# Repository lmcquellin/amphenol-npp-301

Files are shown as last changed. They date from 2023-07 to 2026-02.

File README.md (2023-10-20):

# Use of Amphenol NPP-301 Series Pressure Transducers for Pressure Measurements

## 1. Overview
The NPP-301 series of pressure sensors manufactured by Amphenol Advanced Sensors have demonstrated to be a low cost means of collecting discrete pressure measurements in space constrained locations on wind tunnel models. The transducer is offered in three pressure ranges, 0 – 100 kPa, 0 - 200 kPa, and 0 – 700 kPa.

## 2. Electrical Characteristics

Figure 1 presents the electrical schematic of the NPP-301 as supplied by Amphenol. The large variation in transducer input and output impedance (20% [1]) results in a large amount of transducer-to-transducer variation. Additionally, because the operating pressure can be an order of magnitude lower than the rated pressure, the transducer is having to operate at the extremity of its operating range. The split negative input pins (Pins 4 & 5) allow for the bridge to be compensated through the use of an additional resistor. This compensation allows for the bridge to be balanced at a desired pressure. This has two effects. First, the balanced bridge means that the bridge output voltage is minimised, allowing for greater amplifier dynamic range. Secondly, the bridge compensation process reduces the large variation in transducer output performance between sensors, allowing for simpler amplifiers to be used.

## 3. Frequency Response

Frequency response has not been characterised, but is estimated to be on the order of several kilohertz.

## 4. Bridge Compensation

Bridge compensation is performed using a vacuum cell with a 5 wire feed-through, a mounting PCB or carrier board for connecting to the sensor and a digital multimeter. Details of calibration carrier boards are provided in appendix A.

Bridge compensation is performed as follows:
* If not mounted to a PCB, transducer body is marked for identification. If mounted to a PCB, PCB is typically marked. Transducer is then placed in the integrated circuit socket.
* Mounting PCB or test socket is interconnected through the vacuum cell feed-through, with 5 flying-lead wires available externally for measurement connections.
* Vacuum cell is evacuated to the desired compensation pressure. This is typically $\<$ 100 Pa for wind tunnel testing with evacuated test sectionbs. Ambient temperature during the calibration should also be recorded.
* The following resistances are then measured between pin pairs on the transducer body, using externally available wires. Pin 8 & 2, Pin 8 & 6, Pin 2 & 4, and Pin 6 & 5. Resistance values will typically be in the 4500 - 4900 Ω range and should be recorded to the nearest ohm.

This procedure is repeated for each transducer with the results being populated in a text file called 'resistor_data.txt'. File should be TAB delimited. The resistor_data text file takes the following format:
'''
PIN 8/2  PIN 8/6	PIN 2/4	PIN 6/5
'''

Again, resistance of each measurement element should be recorded in ohms to the nearest ohm. An example have been provided in 'resistor_data.txt'. Once complete, the compensation values for each individual transducer can be determined. To do this, the MATLAB script 'npp_comp.m' is used. Note: 'npp_comp.m' requires 'resval.mat' in order to run successfully. 'resval.mat' is also provided as a comma-separated values file. The script, when run, will evaluate all resistance values present in the 'resistor_data.txt' data file. For each transducer, a suggested compensation resistor value will be provided based on commercially available resistance values (contained in 'resval.mat'), and the branch of the wheatstone bridge this resistance should be provided. The script will also provide a bridge output voltage (Vb) for a given bridge input voltage at the compensated pressure. It is advised that the reported resistance is then recorded in a transducer calibration register (see 'npp_calibration_register_blank.ods') as this will be cleared from the screen when the script is run again. The following provides an example of the script output for a transducer with the values PIN 8/2 = 4726, PIN 8/6 = 4752 PIN 2/4 = 4769 PIN 6/5 = 4742.

```
------
OUTPUT
------
Input Voltage: 5V
Suggested Compensation Resistance: 51 Ohms
Compensation on Leg: 865
Vb: 0.58314 mV
```
Figure 3 presents a revised schematic that includes the compensation resistor and its position within the circuit. It can be seen that the compensation resistor is connected between pins 4 & 5, with the IN- connection point becoming pin 4. Depending on the mounting configuration, the means in which this resistor can be included into the pressure transducer can vary. Two methods are presented here, PCB mounting (subsection 5.1) and ’deadbug’ mounting (subsection 5.2).

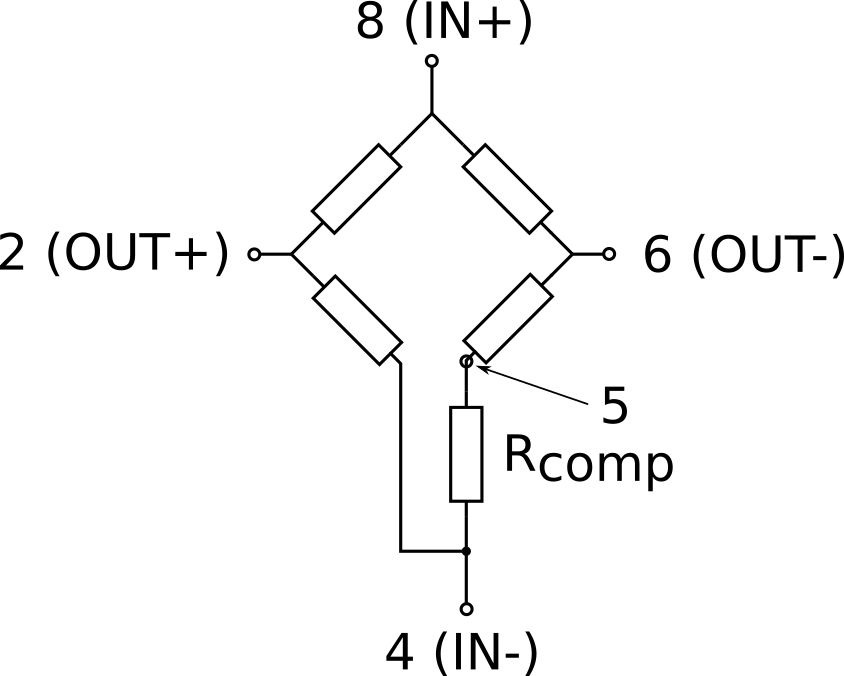
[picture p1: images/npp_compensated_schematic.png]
NPP_Compensated_Schematic


## 5. Packaging and Mounting

The NPP-301 is available in a small-outline 8 (SO8) surface mount package with either a barbless (NPP-301A) or barbed (NPP-301B) pressure port [1]. Dimensions of the barbed and barbless packaging are
available in appendix A. Two mounting options have been explored thus far. Printed circuit board (PCB) mounting and ‘deadbug’ mounting.

### 5.1 PCB Mounting

PCB mounting allows for a transducer to be rigidly mounted to a structure with fasteners. Multiple transducers can also be mounted to a single PCB to simplify interconnectivity and maximise measurement density. The SO8 package size and placement of the barb limits the pitch of an array of transducers to 8 mm. An example of a transducer mounted to a single PCB is provided in Fig. 4. This arrangement where the transducer body is offset from the horizontal centreline of the PCB is done so to place the barb in the horizontal and vertical centre of the board. Four mounting holes suitable for M1.6 fasteners are used in each corner. On the reverse side of the PCB; pads for soldered wire connections are provided, along with pads for surface mount 0402 size compensation resistors. To ensure a adequate pressure connection between the pressure port of the sensor and the pressure tap on the surface of the model, a BS003 o-ring is used to provide a seal. Geometry for the o-ring groove is provided in appendix B. Typical dimensions of a single transducer mounting PCB is also provided in appendix B.

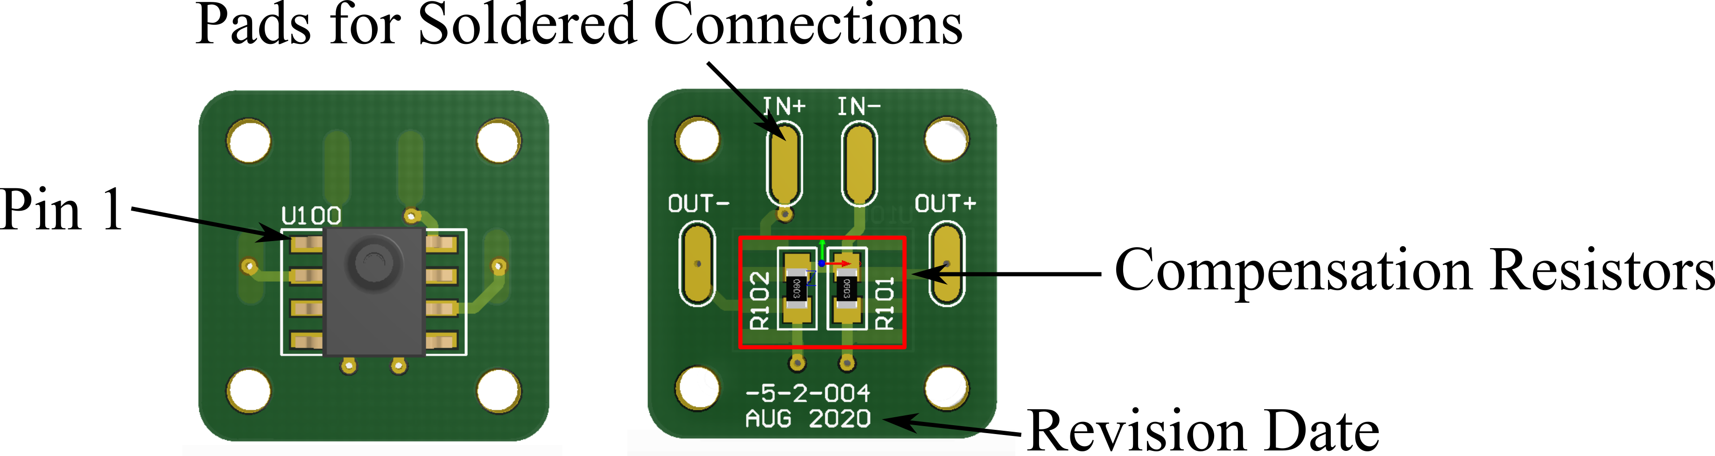
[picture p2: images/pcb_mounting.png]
NPP_PCB_Mounting


### 5.2 Deadbug Mounting

Deadbug mounting, named due to the appearance of an integrated circuit package body upside down, is the other proposed method for interconnecting and mounting the transducer. This mounting type is the most volumetrically efficient, but is more time consuming the manufacture and mounting into a model is permanent. Instructions to assembly a transducer body with wire is provided in appendix C. Transducer bodies are typically bonded into cavities or against panels using epoxy (or other suitable) adhesive. This is depicted in Fig. 5. When using the barbless ‘A’ package, ensuring concentricity between the pressure tap in the panel and port in the transducer can be achieved by using a machined locating pin to locate the transducer during assembly. When using the barbed ‘B’ package, a countersink in the surface is required to accommodate the barb. This countersink ensures port concentricity during mating.

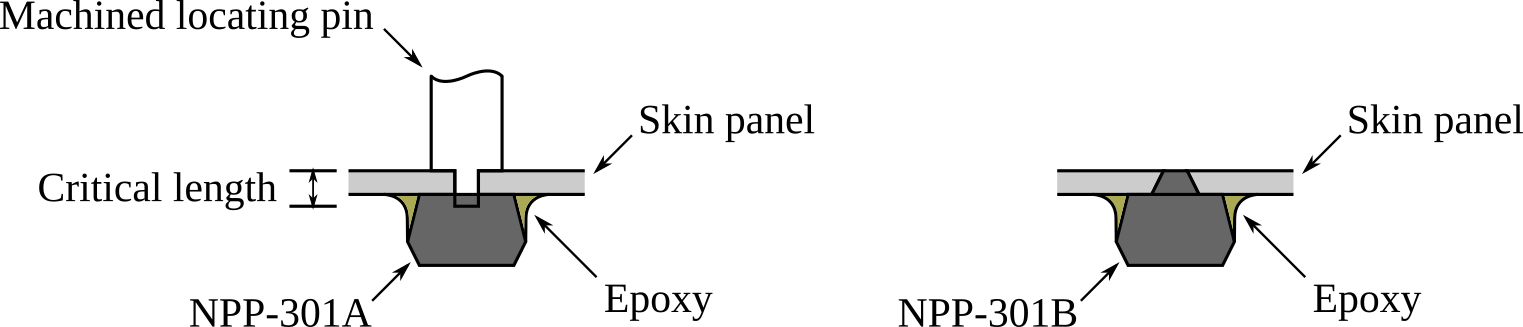
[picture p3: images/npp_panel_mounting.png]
NPP_Panel_Mounting


## References

[1] Amphenol Advanced Sensors. NPP-301 Series Surface Mount Pressure Sensor, 3 2019. web: https://www.amphenol-sensors.com/hubfs/Documents/AAS-920-297B-NovaSensor-NPP-301-031414-web.pdf

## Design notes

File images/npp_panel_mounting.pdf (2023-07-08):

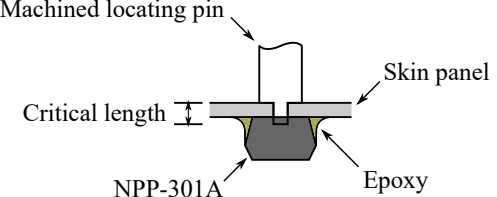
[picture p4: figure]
NPP-301A; Machined locating pin; Skin panel; Epoxy; Critical length
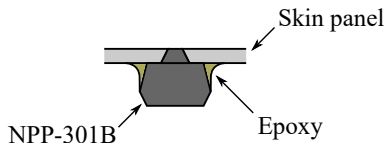
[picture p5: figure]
Skin panel; NPP-301B; Epoxy

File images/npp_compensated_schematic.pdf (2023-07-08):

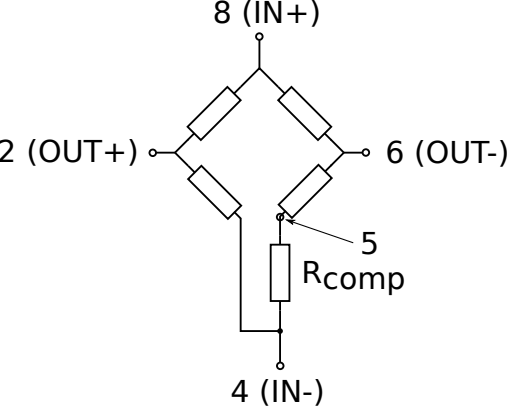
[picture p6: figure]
Rcomp; 2 (OUT+); 6 (OUT-)

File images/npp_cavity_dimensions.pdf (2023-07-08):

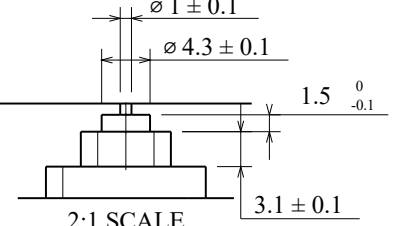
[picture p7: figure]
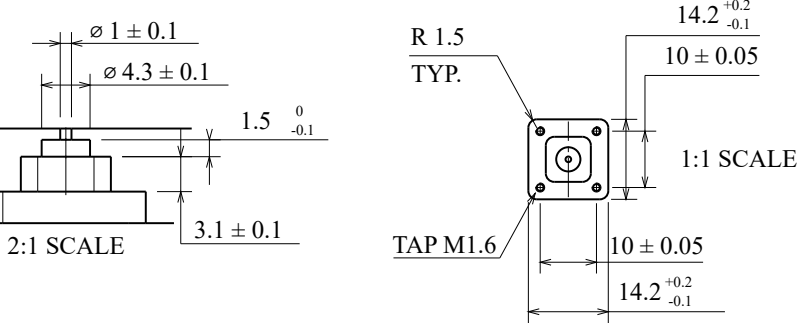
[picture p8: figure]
R 1.5 TYP.; 2:1 SCALE; TAP M1.6; 1:1 SCALE

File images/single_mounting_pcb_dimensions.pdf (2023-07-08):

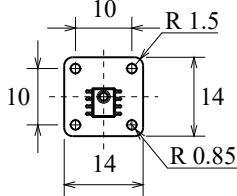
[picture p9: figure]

4.5

1.2

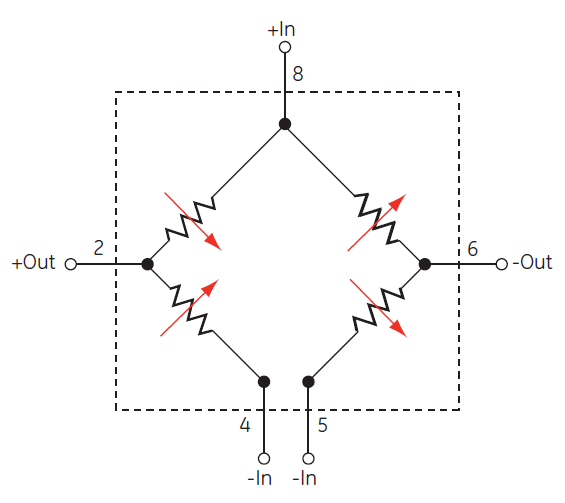
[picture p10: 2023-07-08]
images/npp301_schematic.png

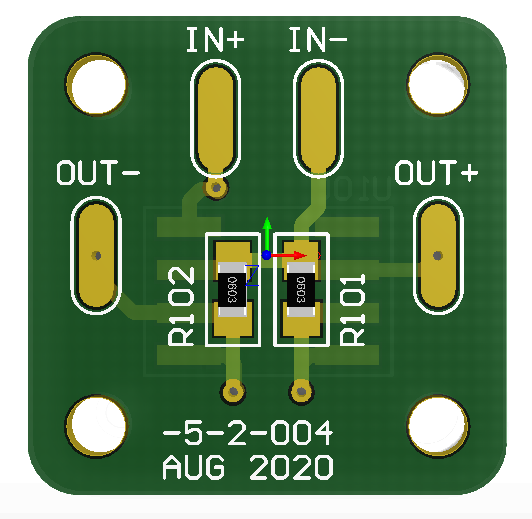
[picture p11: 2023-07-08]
images/npp301b_render_b.png

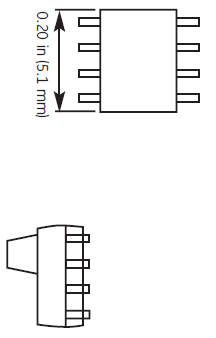
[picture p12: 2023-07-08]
images/301a.png

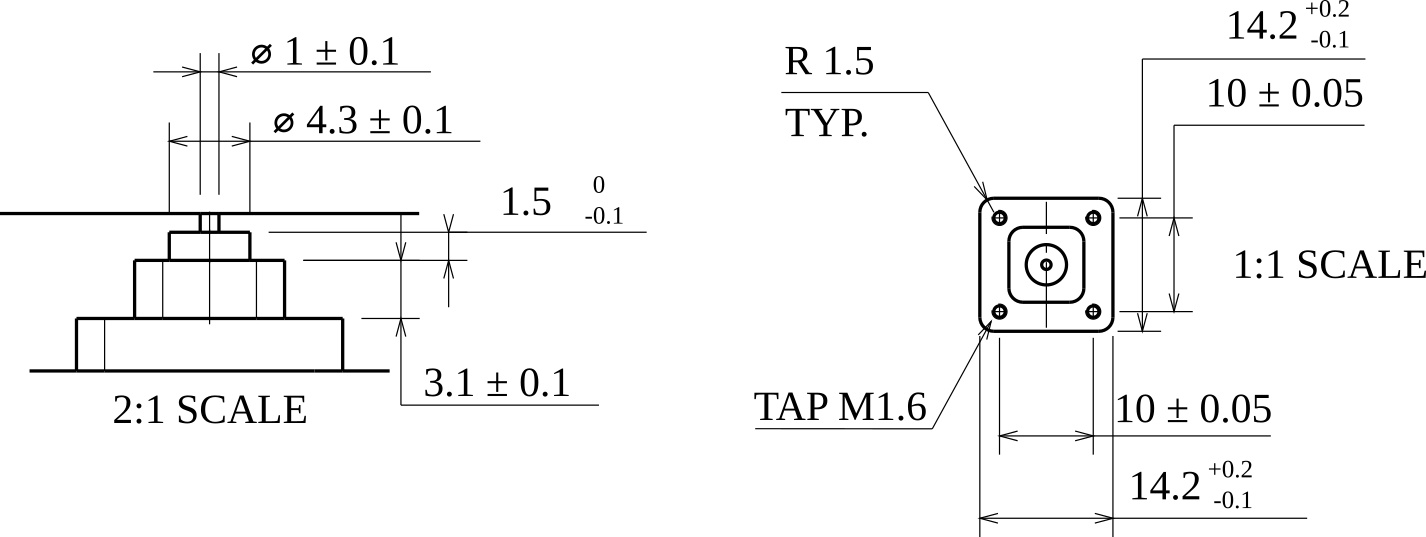
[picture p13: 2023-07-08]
images/npp_cavity_dimensions.png

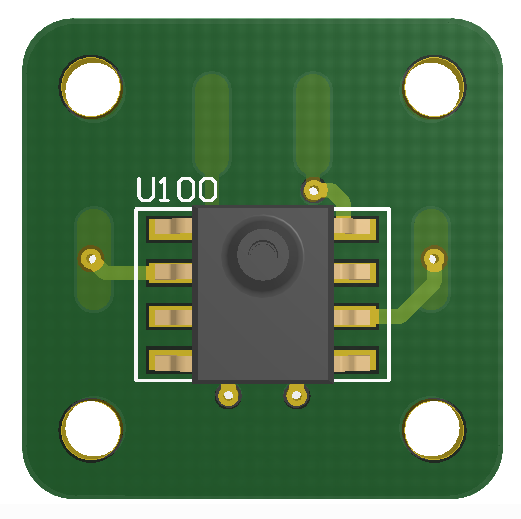
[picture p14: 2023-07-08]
images/npp301b_render_a.png

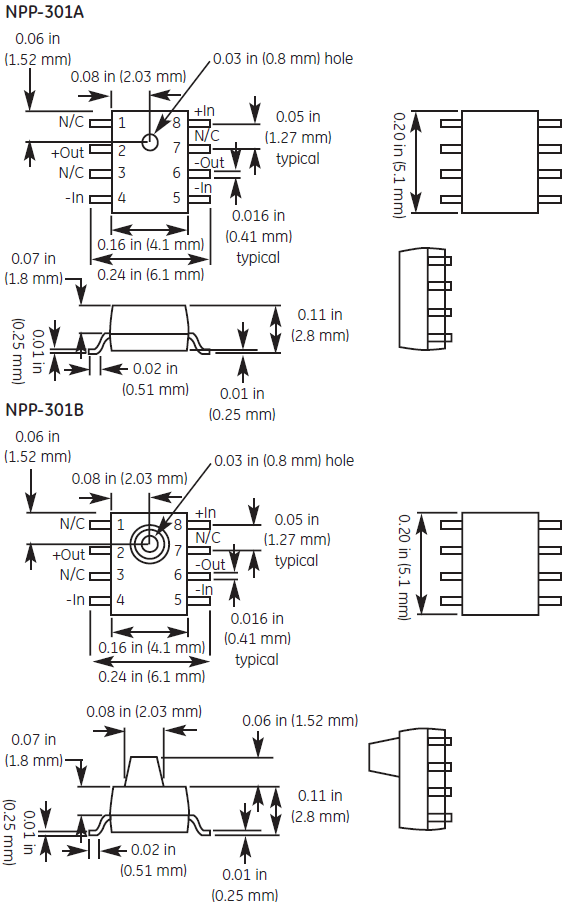
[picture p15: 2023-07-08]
images/npp301_packaging.png

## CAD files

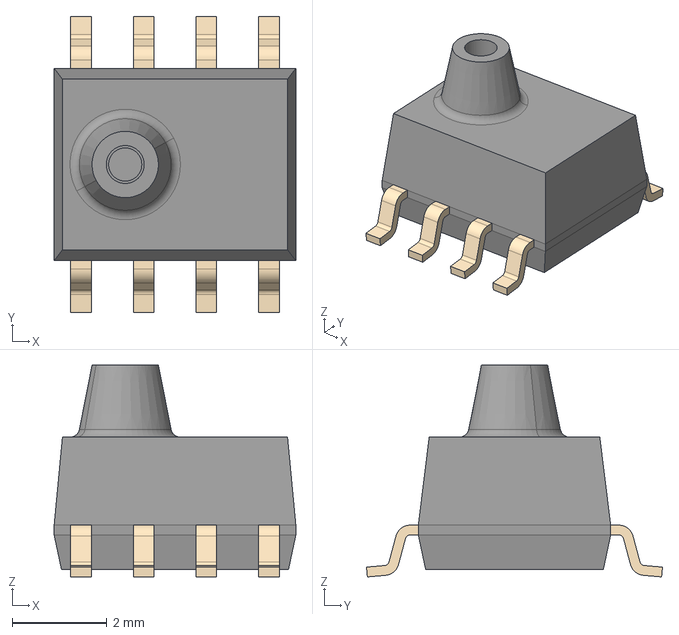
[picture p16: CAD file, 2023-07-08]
3dmodels/npp_301b.stp
5.10 x 6.24 x 4.47 mm

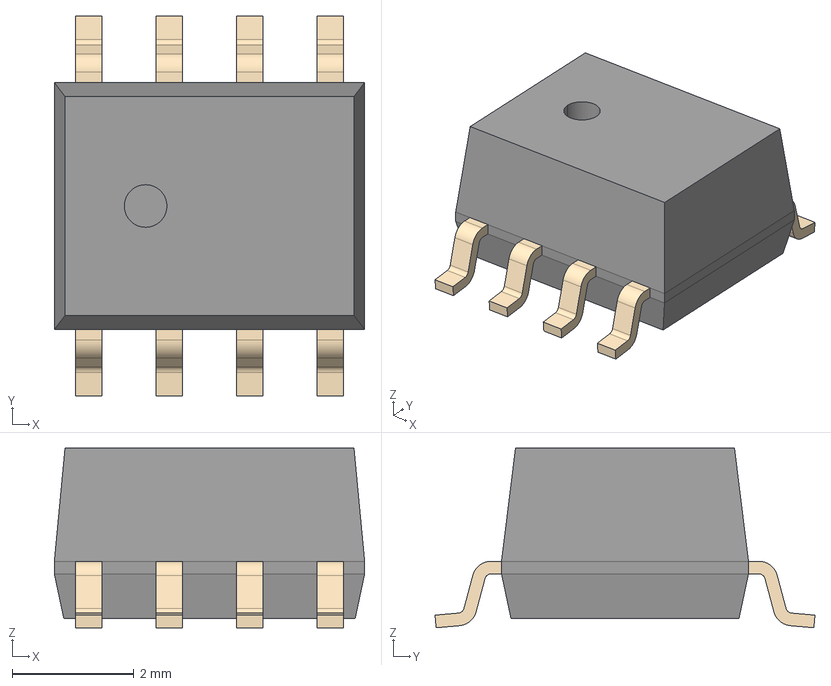
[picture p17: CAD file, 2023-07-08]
3dmodels/npp_301a.stp
5.10 x 6.24 x 2.95 mm

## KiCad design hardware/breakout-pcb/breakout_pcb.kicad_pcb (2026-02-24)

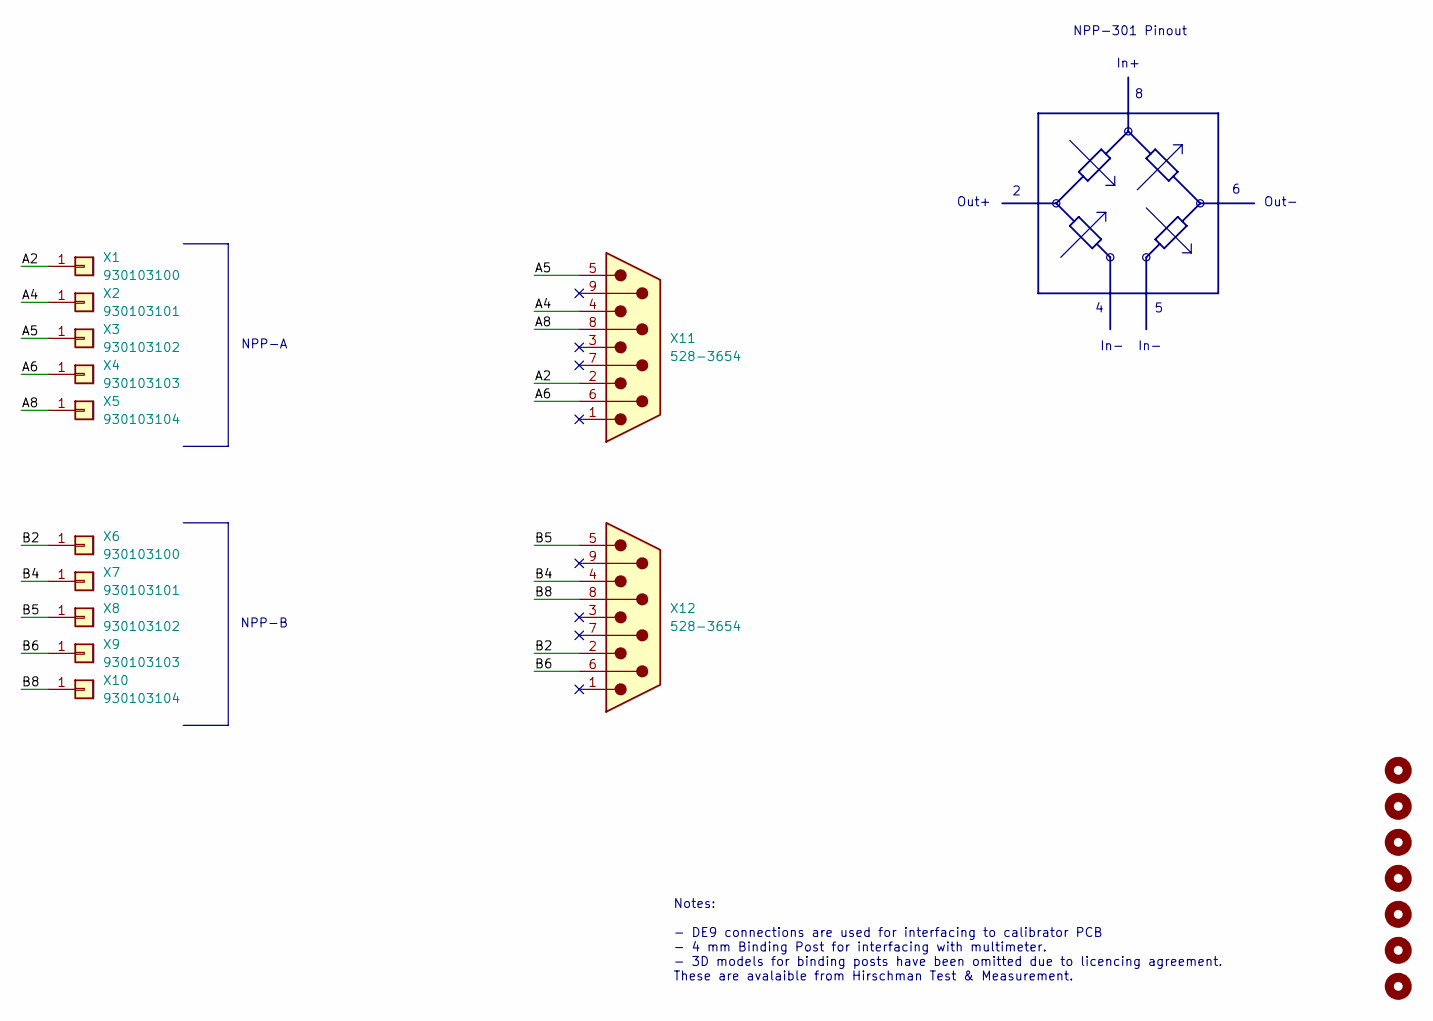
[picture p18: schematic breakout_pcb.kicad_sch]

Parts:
H1, H2, H3, H4, H5, H6, H7: M3; MountingHole_3.2mm_M3_ISO7380_Pad
X1, X6: 930103100; MountingHole_4.3mm_M4_DIN965_Pad
X2, X7: 930103101; MountingHole_4.3mm_M4_DIN965_Pad
X3, X8: 930103102; MountingHole_4.3mm_M4_DIN965_Pad
X4, X9: 930103103; MountingHole_4.3mm_M4_DIN965_Pad
X5, X10: 930103104; MountingHole_4.3mm_M4_DIN965_Pad
X11, X12: 528-3654; DSUB-9_Male_Horizontal_P2.77x2.84mm_EdgePinOffset9.40mm

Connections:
/A2: X1.1, X11.2
/A4: X2.1, X11.4
/A5: X3.1, X11.5
/A6: X4.1, X11.6
/A8: X5.1, X11.8
/B2: X6.1, X12.2
/B4: X7.1, X12.4
/B5: X8.1, X12.5
/B6: X9.1, X12.6
/B8: X10.1, X12.8

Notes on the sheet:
Notes: - DE9 connections are used for interfacing to calibrator PCB - 4 mm Binding Post for interfacing with multimeter. - 3D models for binding posts have been omitted due to licencing agreement. These are avalaible from Hirschman Test & Measurement.
In+
In-
NPP-301 Pinout
NPP-B
Out-
Out+
NPP-A

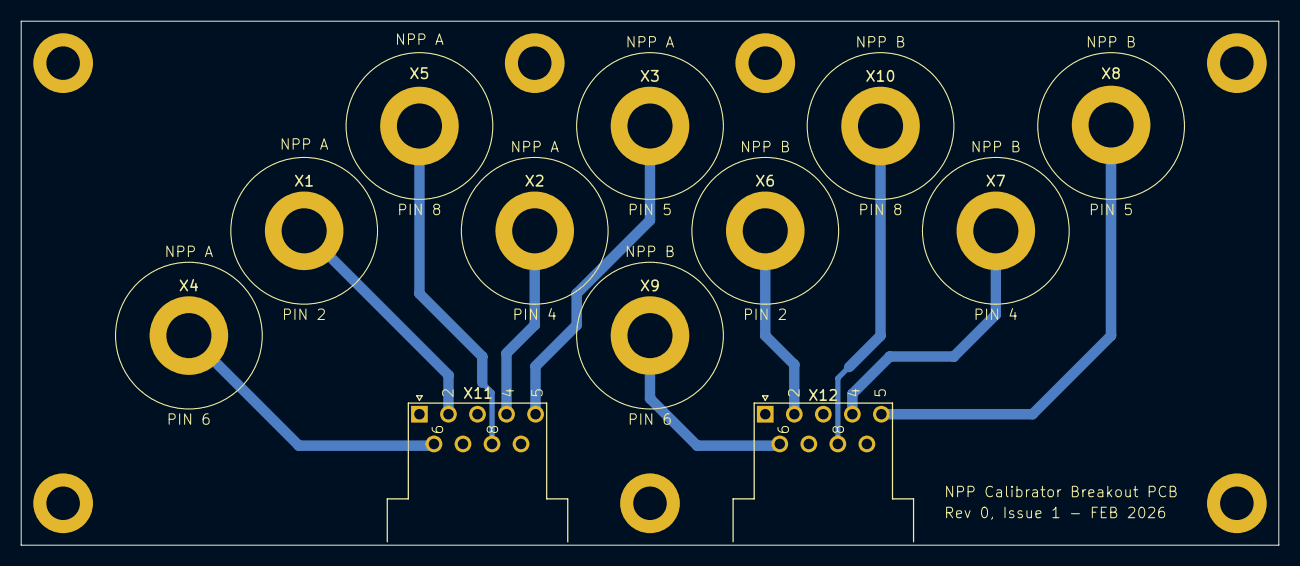
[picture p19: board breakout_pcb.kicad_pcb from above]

Board: 2 copper layers, 120.0 x 50.0 mm, 19 parts (0 on the bottom side), 10 nets.

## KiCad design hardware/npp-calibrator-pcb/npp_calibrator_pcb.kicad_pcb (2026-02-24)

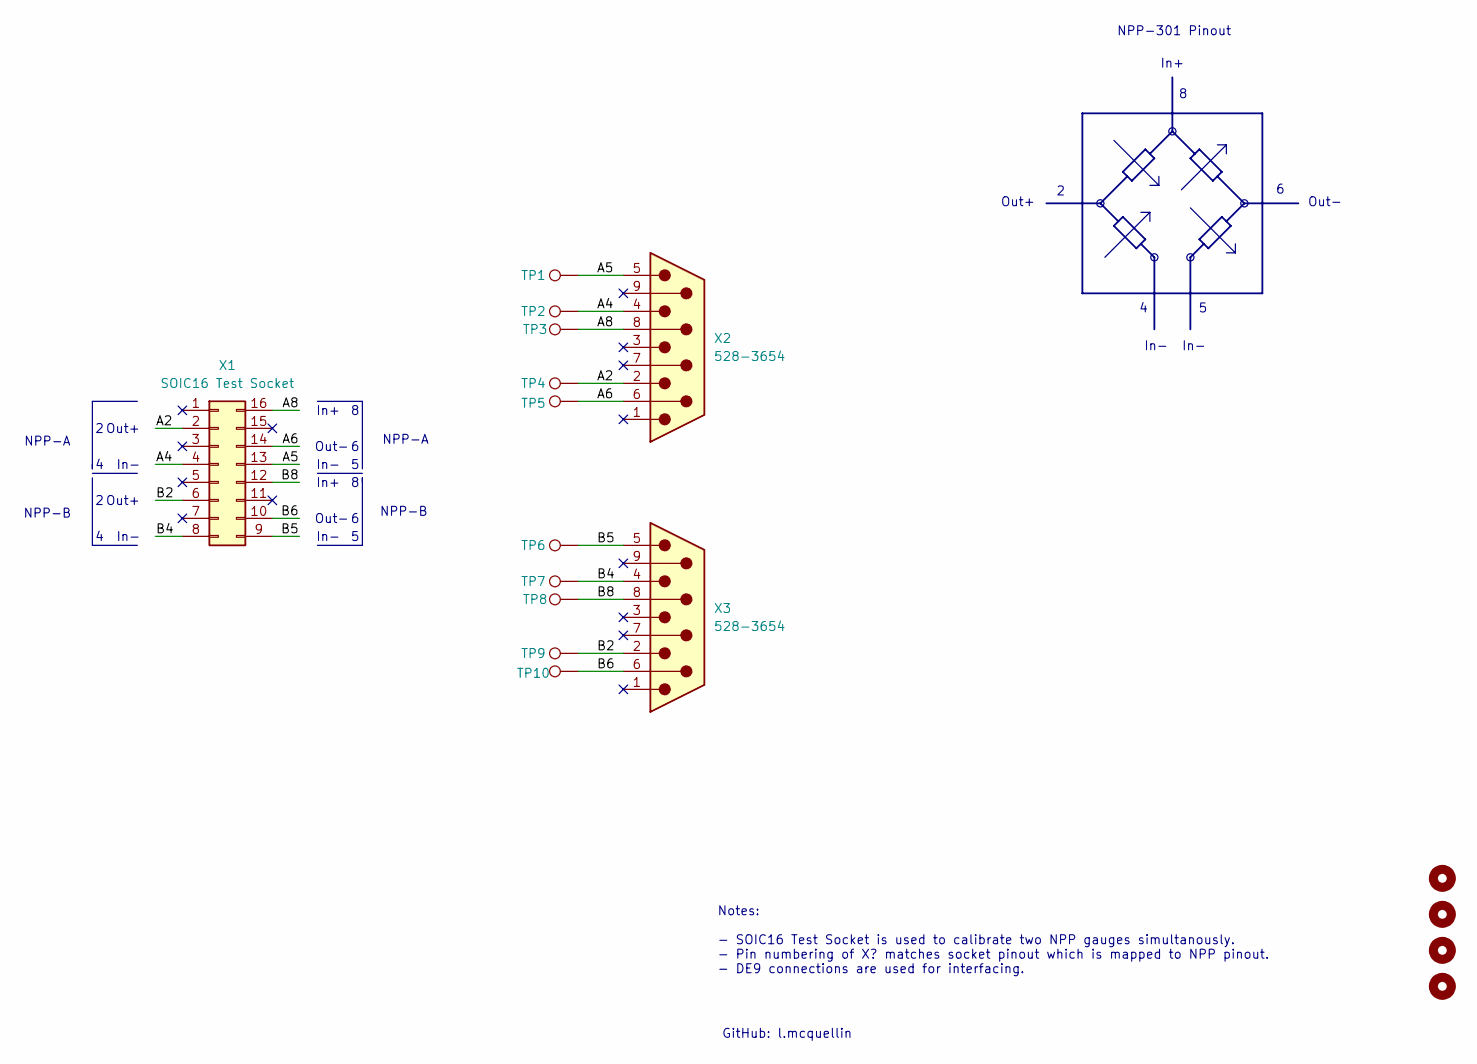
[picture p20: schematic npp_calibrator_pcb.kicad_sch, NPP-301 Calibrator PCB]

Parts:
H1, H2, H3, H4: M3; MountingHole_3.2mm_M3_ISO7380_Pad
TP1, TP2, TP3, TP4, TP5, TP6, TP7, TP8, TP9, TP10: TestPoint; TestPoint_Pad_D2.0mm
X1: SOIC16 Test Socket; PA-SOCKET-SOICN-16-1.27
X2, X3: 528-3654; DSUB-9_Male_Horizontal_P2.77x2.84mm_EdgePinOffset9.40mm

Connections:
/A2: TP4.1, X1.2, X2.2
/A4: TP2.1, X1.4, X2.4
/A5: TP1.1, X1.13, X2.5
/A6: TP5.1, X1.14, X2.6
/A8: TP3.1, X1.16, X2.8
/B2: TP9.1, X1.6, X3.2
/B4: TP7.1, X1.8, X3.4
/B5: TP6.1, X1.9, X3.5
/B6: TP10.1, X1.10, X3.6
/B8: TP8.1, X1.12, X3.8

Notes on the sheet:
In-
NPP-B
In+
NPP-A
Out-
Notes: - SOIC16 Test Socket is used to calibrate two NPP gauges simultanously. - Pin numbering of X? matches socket pinout which is mapped to NPP pinout. - DE9 connections are used for interfacing.
Out+
NPP-301 Pinout
GitHub: l.mcquellin

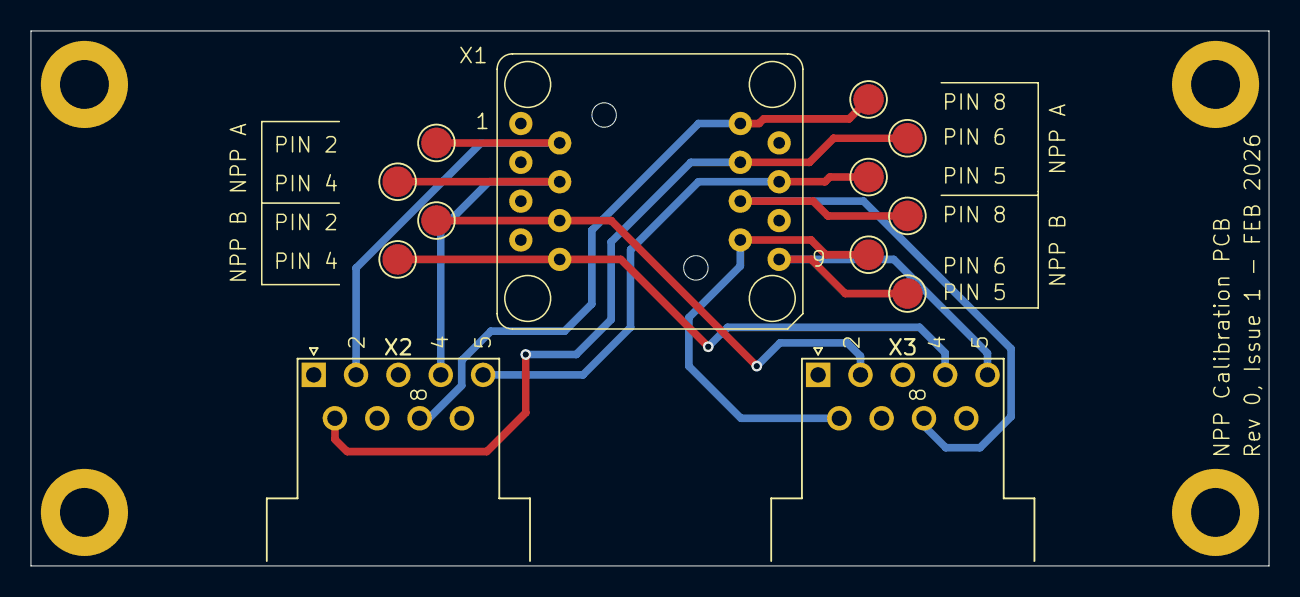
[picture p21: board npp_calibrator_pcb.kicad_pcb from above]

Board: 2 copper layers, 81.0 x 35.0 mm, 17 parts (0 on the bottom side), 10 nets.

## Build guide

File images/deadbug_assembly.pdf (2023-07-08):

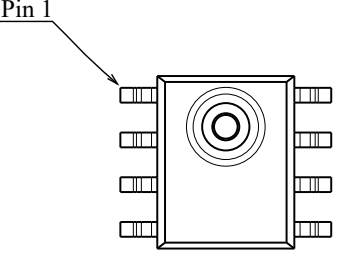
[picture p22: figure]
Pin 1
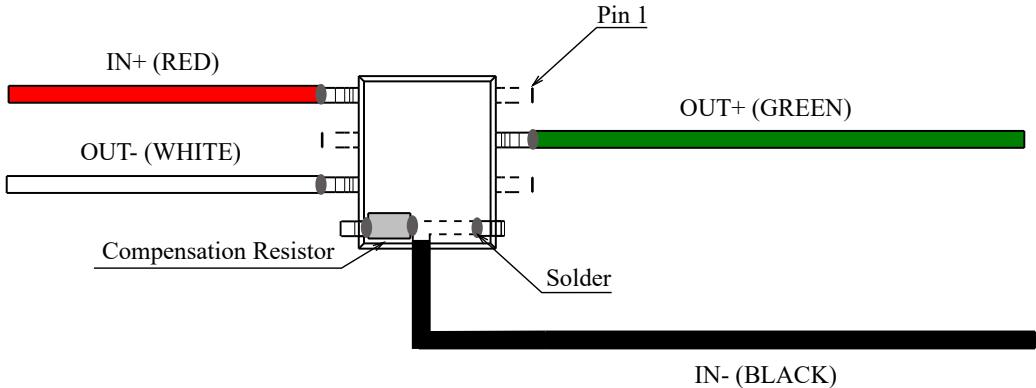
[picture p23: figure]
Pin 1; OUT+ (GREEN); IN- (BLACK); OUT- (WHITE); IN+ (RED); Compensation Resistor; Solder

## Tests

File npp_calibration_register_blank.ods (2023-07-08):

NPP 301 Pressure Transducer Calibration Register, v1.3
Hex Serial must be written on PCB after calibration
Hex Serial | PCB Part Number | Date (DD//MM/YYYY) | Performed By (Firstname Lastname) | Absolute Cell Pressure (Pa) and Temperature (K) | Pins 8 – 2 (Ω) | Pins 8 – 6 (Ω) | Pins 2 – 4 (Ω) | Pins 6 – 5 (Ω) | Comp. Res. Val. (Ω)
00
01
02
03
04
05
06
07
08
09
0A
0B
0C
0D
0E
0F
10
11
12
13
14
15
16
17
18
19
1A
1B
1C
1D
1E
1F
Suggested Wire Colours for Calibration Wiring
 |  | RED (8)
Green(2) |  |  | White(6)
 | Blue(4) |  | Yellow (5)

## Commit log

2023-07-08 Commit of draft readme, associated images and sensor 3d models.
    Draft README, images supporting readme and 3d models of the sensors in .STEP format.
    [npp_301a.stp, npp_301b.stp, resval.csv]
2023-07-08 Adding calibration register and figures for readme.
    [npp_calibration_register_blank.ods]
2025-11-26 add calibrator pcb design files
    [npp_calibrator_pcb.kicad_pcb, npp_calibrator_pcb.kicad_sch]
2026-02-24 Updates to calibration hardware
    [breakout_pcb.kicad_pcb, breakout_pcb.kicad_sch, npp_calibrator_pcb.kicad_pcb, npp_calibrator_pcb.kicad_sch]
